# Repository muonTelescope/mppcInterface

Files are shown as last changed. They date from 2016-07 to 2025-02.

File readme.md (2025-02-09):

[headerIMG]

# MPPC Interface
Measuring and logging photon level light sources is a large part of high energy physics instrumentaiton. This board was created to power and collect data from eight MPPC (Multi Pixel photon counters) or SiPM (Silicon Photomultiplers). Provide coincidence logic and log the data out to a Raspberry Pi.

[img]

This is the main conntroller board of the muon telescope project. This board aimts to replace the current tools used

This is the technical manual for anyone wanting to modify, hack, remix, or program their own SiPM readout. The manual goes into fine detail about construction, assembly, and firmware which should encompass all basic knowledge.

## TOC

## Design
THe design was based off a combiniation of topologies from [sPhenix] design, our previous hardware iterations, and new needs in this version. The MPPCs need a very stable high voltage bias voltage that can be controled over this range in sub-milivolt steps. 

[topologyDiagarm]

This is done thoug hthe top high voltage being controalbe in 1V steps and is common across all eight chanels and a eight channel bottom DAC that provides a controlable virtual ground seperately for each channel.

The anode signal is then sent though a high amplification instrumentation amplifier and then sent to the FPGA's schmitt inputs. The conicidence logic is then done in the FPGA and its outputs are mapped to interupt vectors on the host machine.

### Components
Component selection was built off previous verisons, and the specific use case  of driving [Hamamtsu]'s MPPCs. The major ICs and other unique componets will be descibed below.

#### High Voltage Boost
*Maxim Semiconducr's* [MAX1932] has proven itself with proper layout in pervious interations of the design to provide a stable, controlable, low ripple high voltage for avalanche photodidoes. 

THe chip interanlly has a boost controller, current sensing for a current limit, and a 8b DAC that can be tied in to set the voltage over SPI.

#### Bottom DAC
The other half of the bias voltage is handled by the *Texas Instument* [DAC60508] 8 channel 12b (with a direct drop in replace for up to 16b) digital to analog converter. The linear regulation inside provides a stable output, and using the internal `2.5 V` precsion refrence LSB steps of `0.6 mV` are achived. THe output is highly linear and monotonic. 

The power consuption is also low at `0.6mA/ch` for future power constrained applicaitons.

### Schematic
### Layout
### Mechanics

## Firmware
### High Voltage
### Bottom DAC
### FPGA burning
### Compiling
### Flashing

## Gateware
### Pin connections
### Logic
### Compiling
### Flashing

## Setup
Download and flash a copy of the [Raspberry Pi OS](https://www.raspberrypi.com/software/) using either `dd` or the *Raspberry Pi imager* software.

### Raspberry Pi imager
Select the Raspberry Pi OS Lite and in advanced configuration menu (CTRL+SHIFT+X) enable ssh and add the WiFi credentials if the device will be connected over wireless network.

This video also shows using the software to flash a SD card [How to use Raspberry Pi Imager](https://www.youtube.com/watch?v=ntaXWS8Lk34)

### Advanced install with `dd`
Be very careful using `dd` to copy the image to the SD card. `dd` is a direct bit copy from the imput file to the output file and will indescriminately write over any drives without any checks or protection.

```bash
df -h
sudo umount sdx
sudo dd bs=4M if=<imgPath.img> of=/dev/sdx
```

Enable ssh by creating a blank `ssh` file in the root directory called *boot*.
```bash
cd boot
touch ssh
```

To setup connectingto WiFi on boot, a `/boot/wpa_supplicant.conf` file is created that is automatically copied over to `/etc/wpa_supplicant/wpa_supplicant.conf` on the next boot. 

```bash
nano /boot/wpa_supplicant.conf
```

And add in the relevant configuration.

```
ctrl_interface=DIR=/var/run/wpa_supplicant GROUP=netdev
country=<Insert 2 letter ISO 3166-1 country code here>
update_config=1

network={
 ssid="<Name of your wireless LAN>"
 psk="<Password for your wireless LAN>"
}
```

Insert the SD card into the Raspberry Pi, connect the ethernet cable (if connecting over wired network), and power (unless connecting though POE) and connect to the device using ssh.

You can figure out the IP address in several ways on linux you can use `nmap` or `arp` to search for the Raspberry Pi foundation's OUID (`DC:A6:32` for Raspberry Pi 4, `B8:27:EB` otherwise) on your local subnet. 

```bash
nmap -sP 192.168.1.0/24 | awk '/^Nmap/{ip=$NF}/B8:27:EB/{print ip}'
```

```bash
arp -na | grep -i b8:27:eb
```

For Windows
```cmd
arp -a | findstr b8-27-eb
```

It is also possible to ping a new install with the default hostname if DNS or the bonjour service has the device in its tables.

```bash
ping raspi
```

### Bootstrap
The setup script in the root directory can be run to set up a Raspberry pi from scratch. 

Connect to the raspberry pi using the IP adress found.
```bash
ssh pi@192.168.1.*
sudo apt install -y git
```

```bash
git clone https://github.com/muonTelescope/mppcInterface.git
cd mppcInterface
```

The root directory includes a setup script that updates the operationg system, sets up accounts, installs the toolchain, and enables all required modules. On cloning th repository on the Raspberry Pi, this file shoud be made executable and run.

```bash
chmod +x setup.sh
sudo ./setup.sh
```

expand filwsystem, not needed as pi does it on boot now.

Working buildsystem for gateware
```
Yosys 0.9+3981 (git sha1 7d2097b0, clang 7.0.1-8+rpi3+deb10u2 -fPIC -Os)
arachne-pnr 0.1+328+0 (git sha1 c40fb22, g++ 8.3.0-6+rpi1 -O2)

```

By default the spidev driver on raspberry pi has a maximum transfer size of 4096 bytes.
That might cause problems with this software so to change the default buffersize add spidev.bufsiz=65536 to /boot/cmdline.txt and reboot.
Where 65536 is the maximum size you want to allow.

get mac adress to set hostname
```bash
cat /sys/class/net/eth0/address | cut -d: -f4- | sed 's/://g' | tr [:lower:] [:upper:]
```

channelSelect.sh
```bash
#!/bin/bash

dtparam spi=off

gpio mode 6  out  # CS_DAC
gpio mode 23 out  # CS_MAX1932
gpio mode 5  out  # CS_FPGA

gpio write 6  1
gpio write 23 1
gpio write 5  1

sleep 2

gpio mode 12 out # MOSI
gpio mode 13 out # MISO
gpio mode 14 out # SCK

gpio write 12 $1
gpio write 13 $2
gpio write 14 $3

sleep 2
#rmmod spi_bcm2835
#modprobe spi_bcm2835

dtparam spi=on
```

softwareSerial read python
```python
import sys
import time
import difflib
import pigpio
import datetime
import binascii

RX=17

try:
        pi = pigpio.pi()
        pi.set_mode(RX, pigpio.INPUT)
        pi.bb_serial_read_open(RX, 115200, 8)

        print "DATA - SOFTWARE SERIAL:"
        while 1:
                (count, data) = pi.bb_serial_read(RX)
                if count:
			print str(datetime.datetime.now()) + " " +  str(binascii.hexlify(data))
                time.sleep(0.5)

except Exception as e:
	print(e)
        pi.bb_serial_read_close(RX)
        pi.stop()
```

A controller board for 

This is a continuation of a long process, over five years at this point. It is also part of a much broader set of tools and parts that make up the Muon Telesecope.

## Design

## Hardware
There are three main sections to the hardware. High voltage generation and control, Analog front end, and digital logic conatined in the FPGA.

### Bias Voltage
The MPPCs requre a bias of around 80V (varies greatly by model) with very low ripple and high precision. The gain of the sensors varies with respect to the voltage put across them and even a deviation of 10mV has a significat impact on the gain. The gain is also a function of ambient temperature and the bias needs to be controlabe to within a mV to adjust the gain as temperature changes.

[Gain vs Bias]
[Gain Vs temp chart]

The bias voltage is set though a top high voltage rail and a bottom DAC. This approach allows for a very high precision on the bottom dac along with the range on the top HV. With a 16b DAC, steps of under 100uV are possible, whcih is below the accuracy of most of the rest of the supply

For example to set the voltage to 78.434 the top rail is set to its minimal on voltage to ensure there is never a risk of a forward bias (although with the HV off the output is at 4.5V, the input voltage save the shotky didode drop so the risk is only there if the dac is ser to near its max voltage which may still be below the conduction voltage of the MPPC), then the bottom rail can be set to 1.566V, followed by the HV rail being set to 80V providing a voltage diffreential of 78.434 across the sensor.

#### HV Rail
The top high voltage rail is created using Maxim's [MAX1932] APD bias boost converter. This IC provides a low ripple 5V input to 55V to 110V output (design configurable to 20V-100V) with 8b digital control over SPI and built in current limiting set at 2.5mA.

Using a high amount of filtering on the inputs and outpurs, large bulk capacitors, a tight layout, EMC shields, and sectioned off ground and power planes, the output ripple as well as emitted noise is reduced significantly. The output ripple is well below 1mV.

The voltage range, and step size is dictated with setting R2, R3, and R4. The minimum and maximum voltage set using the equations for on page 7 of the datasheet, and there are 8 bits (256) intermediate values that are possible. The high switching portion was designed with general SMPS design requirements (short high current loops, separated ground planes, EMI shielding) providing a low ripple output (<5mVpp ripple) and no significant back EMF.

The Setting resistors are 0.01% and the chip provides a 0.5% accuracy which needs to be calibrated. The calibration and certification procedure is provided in another section of documention.

[Table of set R values and the range they create]
[Fucntion of byte to voltage with perfect resistors]

#### Bottom DAC

The "Bottom DAC" is the term used to describe the arrangement where the voltage supply at the anode of a reverse biased SiPM is used to "subtract" from the top bias voltage. It is implemented with a eight channel 16b [DAC80508] by Texas Instruments. This provides independent control with a 5V range for each of the eight chanels. 

### Analog Front End
The analog front end amplifier is also highly specilized. The design condierations to be considered are considerable and require specilized parts [MPPC AFE talk]. In the end the selection is a very high bandwidth low noise instrumentation amplifier with a 400x gain. The [OPA846] has a high slew rate of 625V/us and a gain bandwith product of 1.75Ghz providing a adequate bandwith of ~4.3Mhz with our gain. 

[Outfput waveform]

This provides waveforms from over xx photons to reach the 1.4V lower schmitt threadhold of the digital logic 3.3V/2-100mV. 

[Photn and gain calculation]
x photons needed * 40% efficency * 	1.7E6 * 1.602E-19C / nS?	

The aplifier's input in coupled with a DC blocking capacitor and routed very tightly on a single layer to reduce noise and emissions that will easily be amplified with such a high gain. The gain of 400x is acivhed with a 20k and 50R positive feedback in a non-inverting configuration. The output is AC coupled to make sure the output has minimal capacitive loading especially since we are only looking for a hihg speed signal output.

[Routing of AFE]

#### Digital Logic
The digital logic is done with a FPGA and can be reconfigured though gateware based on the detector configuration. The eight channels are connected to the GPIO and the schmitt inputs act as discriminators. The rest of the lines are run to three LEDs that can be used for indication and to the GPIO of the Raspberry Pi.

#### Power supply
The general supply rails are provide dby the host Raspberry pi connector. The entire board uses about 1W across all the modules. The 5V supply, after some back EMF filtering is provided to the HV supply as well as the AFE power module. The 3.3V is used on the FPGA and the signaling Power supply of the DAC.

Very stable +-5V rails are required for the analog front end to have have the low noise it needs. The Analog \pm 5V is seperated to its own power planes and is hevily filtered and decoupled ensuring very little noise that would show amplifed on the output. This supply is generated thougha commerical module which is rated at a low ripple and switching frequency.

A 1.2V linear regulator provides the core voltage to the FPGA.

#### Mounting
The hat is attached to the raspberry pi with four 2.6mm mounting holes form M2.5 screwas nad standoffs. A M2.5x11 standoff provides mounting and clearence. The size of the module is showin in the drawing below, it is the same sizing as a raspberry pi zero.

## Firmware
This repository contains firmware in the form of C++ libraries that can be linked into your own code as well as a basic data logging application that sets up everything and logs the counts to a file. 

#### High Voltage
The SPI bus is connected directly to the MAX1932. Chip select is active low and data is sent MSB (most significant bit first). Sending bytes to it sets the voltage. Setting them to 0x00 turns off the DC-DC converter portion. As values increase to 0xFF (256), the output voltage falls linearly.

```Arduino
//Example Arduino code that loops through all voltages.
//SCLK --> Pin 13 for Uno or Duemilanove
//DIN ---> Pin 11 for Uno or Duemilanove

#include <SPI.h>
#define CS 2 //Any pin

void setup(){
	Serial.begin(9600);
	pinMode(CS, OUTPUT);
	digitalWrite(CS, HIGH);
	SPI.begin();
	SPI.setBitOrder(MSBFIRST);
}

void loop(){
	for(int i = 0 ; i < 256 ; i++){
		digitalWrite(CS, LOW);
		SPI.transfer(i);
		digitalWrite(CS, HIGH);
		Serial.println(i);
	}
}
```

---
In the config file the voltage is set for 25*. 

#### DAC

## Gateware

#### Flashing

##### Clearing
##### Burning
##### File format

##### Compilation
###### Yosys
###### AracnePNR

## Absolute Maximum ratings
## Gaurenteed Ratings
## Manufacturing
### BOM
### PCB Assembly
The board has three fiducials and 1.152mm tooling holes for automated assembly.
### Artwork
### Labeling
## Safety
## Certifications
## Licence
## Attributions

- HV Calibration procedure and certification.

Glossary
MPPC Multi pixel photon counter, Hamamtsu Photonics's 
SiPM
DAC
Bias

# Old Version of docs

A single assembled board breaks out singals and provides all the interfaces that 4 [MPPC Sesnor](https://github.com/Sawaiz/mppcSensor) boards need. The power to each module is supplied via the [MPPC high voltage](https://github.com/Sawaiz/mppcHighVoltage) modules
attached board. It is able to be run independently for testing and debugging, or on a backplane with many others for more channels.

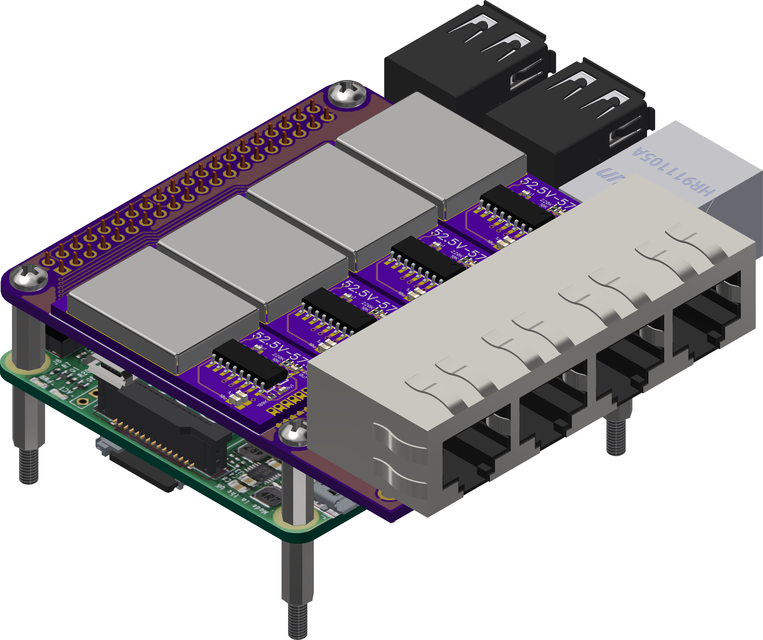
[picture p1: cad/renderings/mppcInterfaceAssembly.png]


## Expansion Format

### SPI
The SPI exapansion format is designed to be infinetly expandable up to the signal propgation length and capactive loading. 

The Design of the SPI system is chained shift registers. The shift registers 

SPI EEPROM lies on each expansion board and has the code needed to interface with it (this sounds beautiful, really).
The EEPROM contains the device enumeration and drivers for all the 8 slots on its adress.
Master downloads drivers 

### I2C

## Hardware
The board attaches directly to a Raspberry Pi using the centered GPIO headers. The Raspberry Pi is mounted to the board via four standoffs. It is a stand alone board requiring no backplane. This board can be mounted via the M5 screw holes around the edge.

### Power
Power is supplied through two pins on the edge connector, or via the micro USB port on board. There is a 600mA buck regulator that provides power when the USB port is used. The board should be powered by 3.3V and a negative power supply module with convert it to -3.3V for the biasing for the op-amps.

### High Voltage
High voltage is supplied through a daughter board. Each channel has a independent voltage source that can be temperature modulated and monitored via the on board ADC. for more information about the modules, read [here](https://github.com/Sawaiz/mppcHighVoltage).

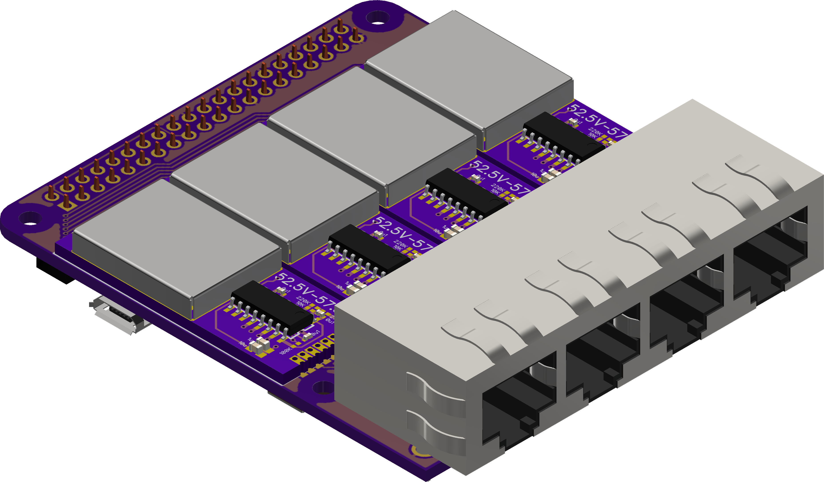
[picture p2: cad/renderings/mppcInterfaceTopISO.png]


### Microcontroller
The side of the board has a Arduino compatible ([ATmega328](http://www.atmel.com/images/Atmel-8271-8-bit-AVR-Microcontroller-ATmega48A-48PA-88A-88PA-168A-168PA-328-328P_datasheet_Complete.pdf)) microcontroller, along with a USB part, USB to UART converter and other supporting circuitry. The button is connected to the reset pin. The programing port on board is a Tag-Connect 6 pin, and is only used for programing the Arduino bootloader.

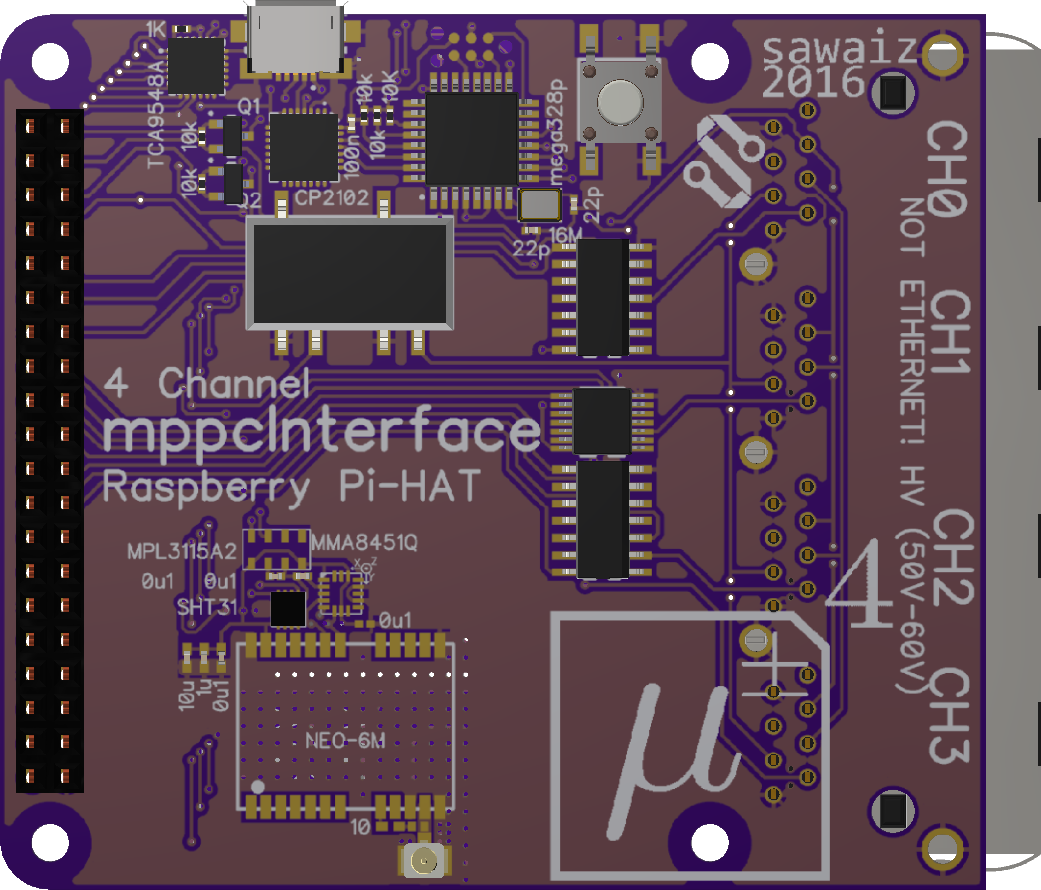
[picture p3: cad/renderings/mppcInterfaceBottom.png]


### I2C Switch
As all the ADC modules on the daughter boards have the same address, a 8 channel I2C switch ([TCA9548A](http://www.ti.com/lit/ds/symlink/tca9548a.pdf)) is used to communicate to them independently. The pins attached to it are referenced as master, as the microcontroller is acting as the master controlling it.

## BOM
The bill of materials is availible in [bom.csv](bom.csv) and is copied into a table below.

| Ref Des                                                                                          | Qty | Manufacturer          | MPN                 | Description                      |
| ------------------------------------------------------------------------------------------------ | ---:| --------------------- | ------------------- | -------------------------------- |
| C1                                                                                               | 1   | Wuerth Elektronik     | 885012105011        | CAP CER 0.22UF 10V X5R 0402      |
| C2                                                                                               | 1   | Wuerth Elektronik     | 885012208116        | CAP CER 0.047UF 100V X7R 1206    |
| C3 C5 C7 C9 C11 C13 C15 C17                                                                      | 8   | Wuerth Elektronik     | 885012205016        | CAP CER 0.047UF 10V X7R 0402     |
| C19                                                                                              | 1   | Samsung               | CL21B105KOFNNNG     | CAP CER 1UF 16V X7R 0805         |
| C20                                                                                              | 1   | Samsung               | CL31B105KCHNNNE     | CAP CER 1UF 100V X7R 1206        |
| C21                                                                                              | 1   | AVX                   | 22201C106MAT2A      | CAP CER 10UF 100V X7R 2220       |
| C22 C24                                                                                          | 2   | Murata                | GRM155C80J106ME11D  | CAP CER 10UF 6.3V X6S 0402       |
| C29 C28 C34 C33 C39 C38 C44 C43 C49 C48 C54 C53 C59 C58 C64 C63                                  | 16  | Wuerth Elektronik     | 885012105016        | CAP CER 0.1UF 16V X5R 0402       |
| C23 C32 C31 C27 C26 C37 C41 C42 C36 C4 C25 C6 C30 C8 C35 C10 C40 C12 C45 C14 C50 C16 C55 C18 C60 | 25  | Samsung               | CL05A105MP5NNNC     | CAP CER 1UF 10V X5R 0402         |
| C65                                                                                              | 1   | TDK                   | C1005X5R1A335M050BC | CAP CER 3.3UF 10V X5R 0402       |
| R1                                                                                               | 1   | Stackpole Electronics | RMCF0402FT1M13      | RES 1.13M OHM 1% 1/16W 0402      |
| R2                                                                                               | 1   | Stackpole Electronics | RMCF0402JT20R0      | RES 20 OHM 5% 1/16W 0402         |
| R3                                                                                               | 1   | Yageo                 | RT0402BRD072K49L    | RES SMD 2.49KOHM 0.1% 1/16W 0402 |
| R4                                                                                               | 1   | Yageo                 | RC0402FR-07806RL    | RES SMD 806 OHM 1% 1/16W 0402    |
| R5                                                                                               | 1   | Yageo                 | RT0402BRD07100KL    | RES SMD 100K OHM 0.1% 1/16W 0402 |
| R6                                                                                               | 1   | TE Connectivity       | CPF0402B23R7E1      | RES SMD 23.7 OHM 0.1% 1/16W 0402 |
| R7 R12 R17 R22 R27 R32 R37 R42                                                                   | 8   | Yageo                 | RT0402DRE071KL      | RES SMD 1K OHM 0.5% 1/16W 0402   |
| R8 R9 R13 R14 R18 R19 R23 R24 R28 R29 R33 R34 R38 R39 R43 R44                                    | 16  | Panasonic             | ERJ-2RKD49R9X       | RES SMD 49.9 OHM 0.5% 1/16W 0402 |
| R10 R15 R20 R25 R30 R35 R40 R45                                                                  | 8   | Stackpole Electronics | RNCF0402DTE20K0     | RES 20K OHM 0.5% 1/16W 0402      |
| R11                                                                                              | 1   | Stackpole Electronics | RMCF0402FT499K      | RES 499K OHM 1% 1/16W 0402       |
| D2                                                                                               | 1   | ON Semiconductor      | FDLL4148            | DIODE GEN PURP 100V 200MA LL34   |
| J1 J2 J3 J4 J5 J6 J7 J8                                                                          | 8   | Hirose                | U.FL-R-SMT-1(40)    | CONN U.FL RCPT STR 50 OHM SMD    |
| J9                                                                                               | 1   | Sullins               | SFH11-PBPC-D20-ST-BK| CONN HDR 40POS 0.1 GOLD PCB      |
| J10                                                                                              | 1   | FCI                   | 54601-906WPLF       | CONN MOD JACK 6P6C R/A UNSHLD    |
| J11                                                                                              | 1   | Harwin                | M20-8760542         | CONN HEADER SMD 10POS 2.54MM     |
| J12                                                                                              | 1   | FCI                   | 54602-908LF         | CONN MOD JACK 8P8C R/A UNSHLD    |
| L1                                                                                               | 1   | Bourns                | SRN4018-151M        | FIXED IND 150UH 320MA 2.4 OHM    |
| L2                                                                                               | 1   | Taiyo Yuden           | CBC3225T102KR       | FIXED IND 1MH 100MA 13 OHM SMD   |
| Q1                                                                                               | 1   | ON Semiconductor      | BSS123L             | MOSFET N-CH 100V 0.17A SOT-23    |
| U1                                                                                               | 1   | Texas Instruments     | DAC60508ZRTER       | IC DAC 12BIT V-OUT 16WQFN        |
| U2                                                                                               | 1   | Microchip             | MIC5504-1.2YM5-TR   | IC REG LINEAR 1.2V 300MA SOT23-5 |
| U3                                                                                               | 1   | Texas Instruments     | LM27761DSGR         | IC REG CHARGE PUMP ADJ 8WSON     |
| U4                                                                                               | 1   | Nexperia              | 74HC595PW-112       | IC 8BIT SHIFT REGISTER 16TSSOP   |
| U5                                                                                               | 1   | Maxim Integrated      | MAX1932ETC+T        | IC REG CTRLR FBR OPT 1OUT 12TQFN |
| U6 U7 U8 U9 U10 U11 U12 U13                                                                      | 8   | Texas Instruments     | OPA846IDBVT         | IC OPAMP VFB 1 CIRCUIT SOT23-5   |
| U14                                                                                              | 1   | Lattice Semiconductor | ICE40LP384-SG32     | IC FPGA 21 I/O 32QFN             |

Aslo availible though [octopart](https://octopart.com/bom-tool/T0iNvVYe) 

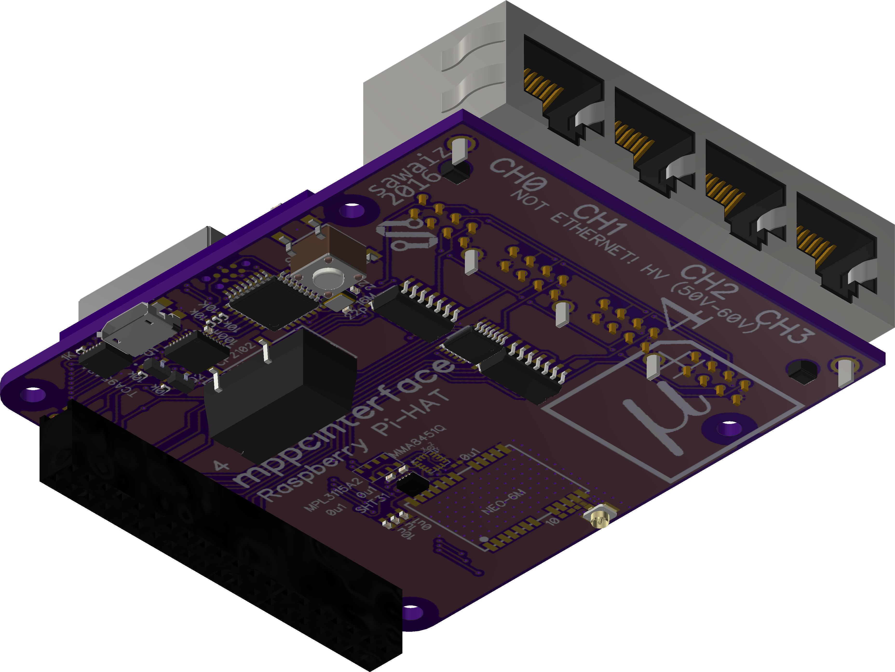
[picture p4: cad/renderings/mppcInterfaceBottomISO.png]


## Software
The device acts as both a master and slave device. It takes instructions from an external I2C bus, and executes them on the AVR microcontroller to set voltages, provide telemetry, and preform closed loop control.

### AVR
The microcontroller on board takes commands sent to the whole module, and forwards them to each daughterboard. It primary control loop involves reading the temperature, finding the associated required bias voltage based on the temperature and setting the voltage on the high voltage supply, then checking if the output voltage is within specification of the required output, and fixing it if not. This loops for all eight channels. Otherwise there is an instruction queue of commands that come into the module.

### Module
The master can communicate to up to 128 slave devices the address is set within software. The master can request the temperature, or current voltage of any of the eight channels on board, select between different voltage to temperature curves, and set the bias voltage, or pulse the LED on the modules.

[mppcInterfaceAssembly]:  cad/renderings/mppcInterfaceAssembly.png  "View of Back of Board"
[mppcInterfaceTopISO]:    cad/renderings/mppcInterfaceTopISO.png    "Direct front view"
[mppcInterfaceBottomISO]: cad/renderings/mppcInterfaceBottomISO.png "Board rendering with EMI shield"
[mppcInterfaceBottom]:    cad/renderings/mppcInterfaceBottom.png    "Board rendering with EMI shield"

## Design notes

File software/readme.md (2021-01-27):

Install nginx
Run webserver with static site for diognostics and settings
Split up files into 1 day increments

Static files with a rest API
    Express
    Top Voltage
    Bottom DAC
    Configuration file selection
    ip adress
    battery percentage
    uptime
    gps
    hostname
    shutdown
mantain local arrays of data
new local log file for each day as backup

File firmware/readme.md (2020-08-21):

## 1 day test 8/18
0x98, 78.56V - Test voltage 
CH0 - 
CH1 - 

## Multi day test 8/19
0x92, 79.775V
CH0 - 0x7880
CH1 - 0x8000

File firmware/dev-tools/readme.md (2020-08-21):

# Development Tools
Development and testing tools run from command line and interact directly with the hardware. The tools provide everything that one can do from the web interface.

## Structure
The code is copied and trimmed down from what is used on the website backend, and is written in javascript. There are bash files that call the functions through nodejs and they make sure it is run with proper permissions and enough arguments.

## Installation
Install the required packages with 
```bash
npm install
```
As these integrate with hardware on a raspberry pi, you will need to build/compile them on the Broadcom chip itself. After the install, you should have a "node_modules" folder in the root project directory.

## Run
Each module is different and requires its own function call. All need to be run as root as hardware GPIO access is privileged

### Current Status
Prints out all the voltages, temperatures, and targets of all eights channels on slave address of 0x08
```bash
sudo ./voltageDump.sh
```
Response is a markdown compatible table
```md
|Board   0x08|  Channel 0 |  Channel 1 |  Channel 2 |  Channel 3 |  Channel 4 |  Channel 5 |  Channel 6 |  Channel 7 |
|------------|------------|------------|------------|------------|------------|------------|------------|------------|
|Target   (V)|   0.000000 |  55.110000 |  55.120000 |  55.170000 |   0.000000 |   0.000000 |   2.887680 |   0.000000 |
|Voltage  (V)|   4.484427 |  55.589808 |  55.323148 |  55.523284 |   0.000000 |   0.000000 |   0.000000 |   0.000000 |
|Temp     (C)|  11.174347 |  16.505951 |  21.479584 |  18.281768 |   0.000000 |   0.000000 |   0.000000 |   0.000000 |

```
The current voltage may not match the target. The firmware on each board should be temperature compensating the bias voltage depending on temperature. The target refers to the voltage at 25C.

### Sensor Temp
Given the channel on a board connected with the slave address of 0x08, it prints out the temperature in degrees Celsius.
```bash
sudo ./getTemp.sh <channel>
```
For example, to read the temperature from the sensor connected to the third port (channel 2, they index from 0).
```bash
sudo ./getTemp.sh 2
```
And the response is just
```bash
21.44754
```

### Current Voltage
Given the channel on a board connected with the slave address of 0x08, it prints out the voltage output from the power supply.
```bash
sudo ./getVoltage.sh <channel>
```
For example, to read the voltage from the sensor connected to the third port (channel 2, they index from 0).
```bash
sudo ./getVoltage.sh 2
```
And the response is just
```bash
55.322936
```

### Read Target Voltage
Given the channel on a board connected with the slave address of 0x08, it prints out the target voltage at 25C.
```bash
sudo ./getTarget.sh <channel>
```
For example, to read the target for the third port (channel 2, they index from 0).
```bash
sudo ./getTarget.sh 2
```
And the response is just
```bash
55.12
```

### Set Target Voltage
Given the channel on a board connected with the slave address of 0x08, it sets the target voltage at 25C.
```bash
sudo ./setTarget.sh <channel>
```
For example, to set the target for the third port (channel 2, they index from 0) to 55.12V.
```bash
sudo ./setTarget.sh 2 55.12
```
There is no response. Reading the target voltage can be used to confirm that the target was changed.

### GPS
If a GPS module is populated, running
```bash
./gpsData.sh
```
Will return
```javascript
{ time: 2016-11-14T07:20:12.000Z,
  latitude: 33.7535,
  longitude: -84.38733333333333,
  altitude: 322.9,
  speedKph: 0.424,
  trueCourse: 'N/A',
  PDOP: 12.12,
  HDOP: 4.79,
  VDOP: 11.13,
  vaild: true }
```
### SHT3X
SHT3X is a temperature and humidity module.
```bash
sudo ./sht3x.sh
```
Returns a JSON formatted object with temperature is Celsius, Fahrenheit, and relative humidity in percent
```javascript 
{ temp: 30004,
  humdity: 18553,
  temp_F: 95.21698329137104,
  temp_C: 35.1205462729839,
  RH: 28.31006332494087 }
```

### MPL3115A2
The MPL3115A2 is a temperature and pressure sensor.
```bash
sudo ./mpl3115a2.sh
``` 
Returns a JSON formatted object containing pressure in pascals and temperature in degrees Celsius
```javascript
{ pressure_H: 94,
  pressure_C: 93,
  pressure_L: 176,
  temp_H: 36,
  temp_L: 128,
  pressure: 386523,
  pascals: 96630.75,
  temp: 584,
  temp_C: 36.5 }
```

### Log Data
The log data module takes two additional parameters. The duration between each log in milliseconds, and the directory location to write the file to.
```bash
sudo ./logdata.sh <duration (ms)> <file location>
```
As the program runs, it also prints the contents of what it writes to the logfile to STDOUT. For example, to run the script with one minute time intervals and store the logfile in a parent directory logs folder run the following.
```bash
sudo ./logData.sh 60000 ../logs/
```
Below is an example of the file `2017-04-24T21:00:07.503Z.log`
```
date,Zero and One,Zero and Two,Zero and Three,One and Two,One and Three,Two and Three,Zero,One,Two,Three,
2017-04-24T21:01:07.625Z,0,0,0,0,37,0,0,830,0,688,
2017-04-24T21:02:07.634Z,0,0,0,0,44,0,0,843,0,725,
2017-04-24T21:03:07.639Z,0,0,0,0,40,0,0,869,0,717,
2017-04-24T21:04:07.643Z,0,0,0,0,36,0,0,810,0,688,
2017-04-24T21:05:07.647Z,0,0,0,0,42,0,0,860,0,673,
2017-04-24T21:06:07.652Z,0,0,0,0,47,0,0,888,0,728,
```

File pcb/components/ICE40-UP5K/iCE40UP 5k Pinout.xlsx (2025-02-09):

# Pin Out For iCE5UP5K (iCE40 UltraPlus - 5K)
# Revision 0.4 - Remove FWG49
# Revision 1.1 - Fix RGB pins, swapped C5 & A5 pins as well as 39 & 41
# Updated Jun 19, 2017
FNC | Pin Type | BANK | Differential Pair | UWG30 | SG48
IOB_0a | PIO | 2 |  | E5 | 46
IOB_2a | DPIO | 2 | TRUE_of_IOB_3b | D5 | 47
IOB_3b_G6 | DPIO/GBIN | 2 | COMP_of_IOB_2a | F5 | 44
IOB_4a | DPIO | 2 | TRUE_of_IOB_5b | - | 48
IOB_5b | DPIO | 2 | COMP_of_IOB_4a | - | 45
IOB_6a | PIO | 2 |  | - | 2
IOB_8a | DPIO | 2 | TRUE_of_IOB_9b | - | 4
IOB_9b | DPIO | 2 | COMP_of_IOB_8a | E4 | 3
IOB_10a | DPIO | 1 | TRUE_of_IOB_11b | C3 | -
IOB_11b_G5 | DPIO/GBIN | 1 | COMP_of_IOB_10a | F4 | -
creset_b | CONFIG | 1 |  | F3 | 8
IOB_12a_G4_CDONE | CONFIG/DPIO/GBIN | 1 | TRUE_of_IOB_13b | D3 | -
CDONE | CONFIG | 1 |  | - | 7
IOB_13b | DPIO | 1 | COMP_of_IOB_12a | E3 | 6
IOB_16a | PIO | 1 |  | - | 9
IOB_18a | PIO | 1 |  | - | 10
IOB_20a | PIO | 1 |  | - | 11
IOB_22a | DPIO | 1 | TRUE_of_IOB_23b | - | 12
IOB_23b | DPIO | 1 | COMP_of_IOB_22a | - | 21
IOB_24a | DPIO | 1 | TRUE_of_IOB_25b | B1 | 13
IOB_25b_G3 | DPIO/GBIN | 1 | COMP_of_IOB_24a | F2 | 20
IOB_29b | PIO | 1 |  | - | 19
IOB_31b | PIO | 1 |  | - | 18
IOB_32a_SPI_SO | DPIO/CONFIG_SPI | 1 |  | F1 | 14
IOB_33b_SPI_SI | DPIO/CONFIG_SPI | 1 |  | E1 | 17
IOB_34a_SPI_SCK | DPIO/CONFIG_SPI | 1 |  | D1 | 15
IOB_35b_SPI_SS | DPIO/CONFIG_SPI | 1 |  | C1 | 16
VCCPLL | VCCPLL |  |  | B2 | 29
IOT_36b | DPIO/I3C | 0 | COMP_of_IOT_37a | A1 | 25
IOT_37a | DPIO/I3C | 0 | TRUE_of_IOT_36b | A2 | 23
IOT_38b | DPIO | 0 | COMP_of_IOT_39a | - | 27
IOT_39a | DPIO | 0 | TRUE_of_IOT_38b | - | 26
IOT_41a | PIO | 0 |  | - | 28
IOT_42b | DPIO | 0 | COMP_of_IOT_43a | - | 31
IOT_43a | DPIO | 0 | TRUE_of_IOT_42b | - | 32
IOT_44b | DPIO | 0 | COMP_of_IOT_45a | - | 34
IOT_45a_G1 | DPIO/GBIN | 0 | TRUE_of_IOT_44b | - | 37
IOT_46b_G0 | DPIO/GBIN | 0 |  | B3 | 35
IOT_47a | PIO | 0 |  | A4 | -
IOT_48b | DPIO | 0 | COMP_of_IOT_49a | - | 36
IOT_49a | DPIO | 0 | TRUE_of_IOT_48b | - | 43
IOT_50b | DPIO | 0 | COMP_of_IOT_51a | - | 38
IOT_51a | DPIO | 0 | TRUE_of_IOT_50b | - | 42
RGB2 | LED | 0 |  | C5 | 41
RGB1 | LED | 0 |  | B5 | 40
RGB0 | LED | 0 |  | A5 | 39
GND | GND | GND |  | B4 | Paddle
GND | GND | GND |  | E2 | Paddle
GND | GND | GND |  | - | Paddle
VCC | VCC | VCC |  | C2 | 5
VCC | VCC | VCC |  | - | 30
VCCIO_0 | VCCIO | 0 |  | A3 | 33
SPI_Vccio1 | VCCIO | 1 |  | D2 | 22
VCCIO_2 | VCCIO | 2 |  | C4 | 1
VPP_2V5 | VPP | VPP |  | D4 | 24
*SG48 GND is connected to package paddle

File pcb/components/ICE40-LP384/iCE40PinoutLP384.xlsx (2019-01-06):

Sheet: Pinout
iCE40 Pinout LP384
Ball Function | Pin Type | Bank | (SG32) 32-Pin QFN Ball Number | (CM36) 36-Ball ucBGA Ball Number | (CM49) 49-Ball ucBGA Ball Number
IOL_1A | DPIO | 3 | - | - | -
IOL_1B | DPIO | 3 | - | - | -
IOL_2A | DPIO | 3 | 2 | B1 | A1
IOL_2B | DPIO | 3 | 1 | A1 | B1
IOL_3A | DPIO | 3 | - | - | C2
IOL_3B | DPIO | 3 | - | - | B2
IOL_4A | DPIO | 3 | 5 | C2 | C1
IOL_4B_GBIN7 | GBIN | 3 | 6 | C1 | D2
IOL_5A_GBIN6 | GBIN | 3 | 8 | D1 | E2
IOL_5B | DPIO | 3 | 7 | E1 | D1
IOL_6A | DPIO | 3 | - | - | -
IOL_6B | DPIO | 3 | - | - | -
IOL_7A | DPIO | 3 | - | - | F1
IOL_7B | DPIO | 3 | - | - | D3
IOL_8A | DPIO | 3 | - | - | G1
IOL_8B | DPIO | 3 | - | - | F2
IOB_16 | PIO | 2 | - | - | -
IOB_17 | PIO | 2 | - | - | -
IOB_18 | PIO | 2 | - | - | -
IOB_19 | PIO | 2 | - | - | -
IOB_20 | PIO | 2 | - | F2 | G3
IOB_21_GBIN5 | GBIN | 2 | - | E2 | F3
IOB_22_GBIN4_CBSEL0 | GBIN | 2 | - | E3 | F4
IOB_23_CBSEL1 | PIO | 2 | - | F3 | G4
CDONE | CONFIG | 2 | 11 | C4 | D5
CRESET_B | CONFIG | 2 | 10 | F4 | G5
IOB_24_SDO | SPI | SPI | 12 | E4 | F5
IOB_25_SDI | SPI | SPI | 13 | F5 | G6
IOB_26_SCK | SPI | SPI | 15 | E5 | F6
IOB_27_SS | SPI | SPI | 14 | D5 | E6
VCC_SPI | SPI | SPI | 16 | F6 | G7
IOR_28 | PIO | 1 | - | - | -
IOR_29 | PIO | 1 | - | - | -
IOR_30 | PIO | 1 | - | - | -
IOR_31 | PIO | 1 | - | - | -
IOR_33 | PIO | 1 | - | E6 | F7
IOR_34 | PIO | 1 | 18 | D6 | E7
IOR_35_GBIN3 | GBIN | 1 | 19 | C5 | D6
IOR_36_GBIN2 | GBIN | 1 | 20 | B4 | D7
IOR_37 | PIO | 1 | - | B5 | C6
IOR_38 | PIO | 1 | 22 | B6 | C7
IOR_39 | PIO | 1 | 23 | C6 | C5
IOR_40 | PIO | 1 | - | - | -
IOR_41 | PIO | 1 | - | - | -
IOR_42 | PIO | 1 | - | - | -
IOR_43 | PIO | 1 | - | - | -
VPP_2V5 | VPP | VPP | 24 | A6 | B7
VPP_FAST | VPP | VPP | - | - | -
IOT_44 | PIO | 0 | - | - | A7
IOT_45 | PIO | 0 | 26 | - | A6
IOT_46 | PIO | 0 | - | - | D4
IOT_47 | PIO | 0 | 27 | - | A5
IOT_48 | PIO | 0 | - | - | A4
IOT_49_GBIN0 | GBIN | 0 | 29 | B3 | B4
IOT_50_GBIN1 | GBIN | 0 | 30 | A3 | C4
IOT_51 | PIO | 0 | - | - | A3
IOT_52 | PIO | 0 | 32 | A2 | A2
IOT_53 | PIO | 0 | 31 | C3 | B3
IOT_54 | PIO | 0 | - | - | -
IOT_55 | PIO | 0 | - | - | -
GND | GND | GND | 3 | D2 | E3
GND | GND | GND | 21 | D3 | E4
GND | GND | GND | - | D4 | E5
GND | GND | GND | - | - | -
VCC | VCC | VCC | 25 | B2 | C3
VCC | VCC | VCC | - | - | E1
VCC | VCC | VCC | - | - | -
VCCIO_0 | VCCIO | VCCIO | 28 | A4 | B5
VCCIO_1 | VCCIO | VCCIO | 17 | A5 | B6
VCCIO_2 | VCCIO | VCCIO | 9 | - | -
VCCIO_3 | VCCIO | VCCIO | 4 | - | -
VCCIO_2_3 | VCCIO | VCCIO | - | F1 | G2
NC | NC | NC | - | - | -
NC | NC | NC | - | - | -
NC | NC | NC | - | - | -
NC | NC | NC | - | - | -
NC | NC | NC | - | - | -
NC | NC | NC | - | - | -
NC | NC | NC | - | - | -
NC | NC | NC | - | - | -
NC | NC | NC | - | - | -
NC | NC | NC | - | - | -

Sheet: Revision History
Version | Date | Description
1.1 | 2013-06-27 | Removal of CM81 package. Included package ordering code.
1.0 | 2013-03-13 | Initial Release

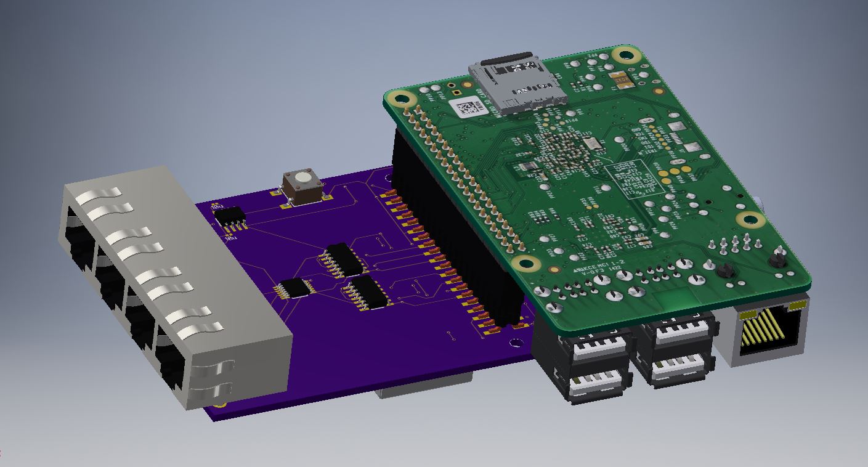
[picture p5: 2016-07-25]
cad/renderings/mppcInterfaceIso.jpg

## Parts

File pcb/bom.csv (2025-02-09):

Designator | Type | Package | Quantity | Description | MPN | LCSC | Vendor | Notes
C1 C3 C5 C9 C25 C28 C33 C30 C38 C35 C43 C40 C48 C45 C50 C53 C55 C58 C60 C63 C66 C67 | SMD | C-0402 | 22 | CAP: 0402 0u1 16V MLCC | CL05B104KO5NNNC | C1525 | Open
C11 | SMD | C-0805 | 1 | CAP: 0805 47n 100V MLCC | CL21B473KCFNNNE | C376987 | Open
C12 | SMD | C-1206 | 1 | CAP: 1206 1u 100V MLCC | CL31B105KCHNNNE | C13832 | Open
C13 | SMD | C-2220 | 1 | CAP: 2220 10u 100V MLCC | FS55X106K101EGG | C2843466 | Open
C14 C18 C17 | SMD | C-0805 | 3 | CAP: 0805 4u7 25V MLCC | CL21A475KAQNNNE | C1779 | Open
C2 C4 C6 C7 C10 C15 C16 C19 C20 C24 C26 C8 C29 C31 C34 C36 C39 C41 C44 C46 C49 C51 C54 C56 C59 C61 | SMD | C-0402 | 26 | CAP: 0402 1u 16V MLCC | CL05A105KP5NNNC | C52923 | Open
C21 | SMD | C-0402 | 1 | CAP: 0402 0u22 16V MLCC | 8.85012E+11 | C16772 | Open
C23 | SMD | C-0805 | 1 | CAP: 0805 0u1 16V MLCC | CL21B104KACNNNC | C49678 | Open
C27 C32 C37 C42 C47 C52 C57 C62 | SMD | C-0402 | 8 | CAP: 0402 0u1 100V MLCC | GRM155R62A104KE14D | C162179 | Open
C68 C22 C64 C65 | SMD | C-0805 | 4 | CAP: 0805 1u 16V MLCC | CL21B105KOFNNNG? | C28323 | Open
D3 D1 D2 | SMD | D-0402 | 3 | LED: 0402 RED | 150040RS73240 | C165980 | Open
D4 | SMD | SOD-80 | 1 | D: LL4148 100V Fast | LL4148-M-08 | C9808 | Open
J1 J2 J3 J4 J5 J6 J7 J8 | SMD | U.FL | 8 | CON: U.FL Coax | U.FL-R-SMT-1(40) | C88374 | Open
J9 | THT | 20x2 2.54mm | 1 | CON: 40pin Stacking | 1528-1385-ND | C3165 | Open
L1 | SMD | SRN4018 | 1 | IND: 150uH 350mA Sat | SRN4018-151M | C285835 | Bourns
L2 | SMD | L-1210 | 1 | IND: 1210 1mH | CBC3225T102KR | C114766 | Open
L3 L4 | SMD | L-0805 | 2 | IND: 0805 47u | LBR2012T470K | C14304 | Open
L7 L6 L5 | SMD | L-0805 | 3 | IND: 0805 10u | MLZ2012M100WT000 | C1046 | Open
Q1 | SMD | SOT-23-3 | 1 | Q: BSS123L | BSS123LT1G | C78755 | Open
R1 | SMD | R-0402 | 1 | RES: 0402 806R 1% | RMCF0402FT806R | C150511 | Open
R2 | SMD | R-0402 | 1 | RES: 0402 100K 0.1% | RT0402BRE07100KL | C525709 | Open
R3 | SMD | R-0402 | 1 | RES: 0402 2K49 0.1% | RMCF0402FT2K49 | N/A | Open
R4 | SMD | R-0402 | 1 | RES: 04002 20R 5% | RMCF0402JT20R0 | C25150 | Open
R5 | SMD | R-0402 | 1 | RES:0402 2K37 0.1% | RT0402BRD072K37L | N/A | Open
R6 R10 R14 R18 R22 R26 R30 R34 | SMD | R-0402 | 8 | RES: 0402 1K 5% | CRG0402J1K0 | C279987 | Open
R7 R8 R12 R11 R15 R16 R19 R20 R23 R24 R28 R27 R32 R31 R36 R35 | SMD | R-0402 | 16 | RES: 0402 49R9 0.1% | RT0402BRD0749R9L | C490832 | Open
R9 R13 R17 R21 R25 R29 R33 R37 | SMD | R-0402 | 8 | RES: 0402 20K 0.1% | RT0402BRD0720KL | C490819 | Open
SH1 | SMD | S03-30100300R | 1 | S03-30100300R | S03-30100300R | N/A | Harwin | Do not populate or purchase
U1 U2 U3 U4 U5 U6 U7 U8 | SMD | SOT-23-5 | 8 | AMP: OPA846 | OPA846IDBVR | C205997 | TI
U10 | SMD | SOT-23-5 | 1 | PWR: MIC5504-1.2YM5 | MIC5504-1.2YM5-TR | N/A | Microchip
U11 | SMD | TQFN-12 | 1 | PWR: MAX1932 | MAX1932ETC+T | N/A | Maxim
U12 | SMD | WQFN-16 | 1 | U: DAC60508ZRTE | DAC60508ZRTET | N/A | TI
U13 | THT | MEA1-D | 1 | PWR: MEA1D0505DC | MEA1D0505DC | N/A | MuRata
U9 | SMD | QFN32 | 1 | U: ICE40-LP384-SG32 | ICE40LP384-SG32 | N/A | Lattice

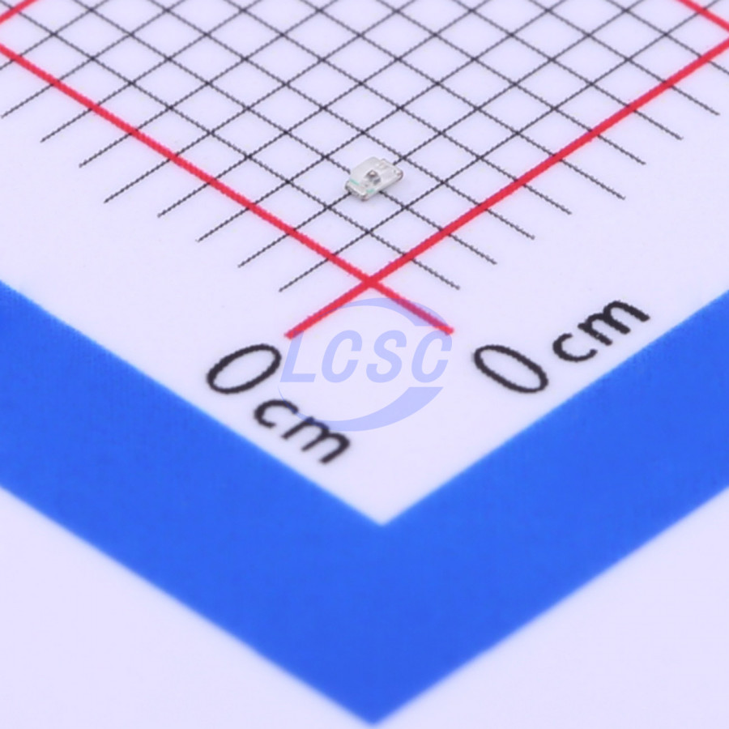
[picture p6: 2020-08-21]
pcb/components/BL-HUB37A-AV-TRB/BL-HUB37A-AV-TRB.jpg

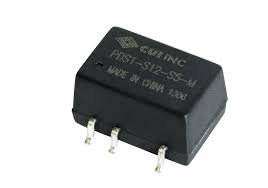
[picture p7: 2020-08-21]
pcb/components/PDS1-M/PDS1-M.jpg

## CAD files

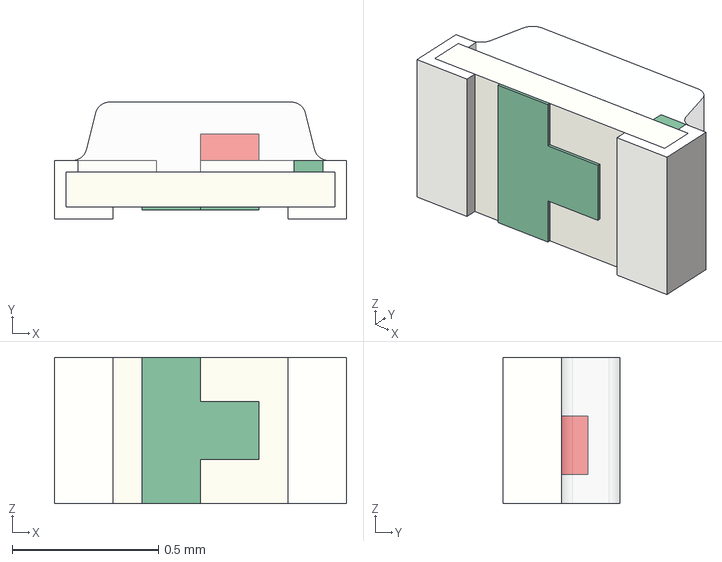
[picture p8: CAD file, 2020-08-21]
pcb/components/BL-HUB37A-AV-TRB/BL-HUB37A-AV-TRB.stp
1.00 x 0.4 x 0.5 mm

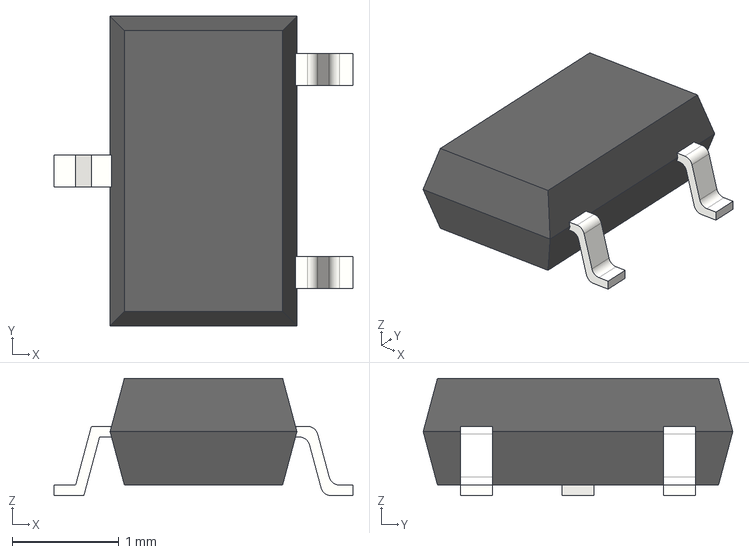
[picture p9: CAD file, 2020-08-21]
pcb/components/BSS123L/SOT-23-3.stp
2.80 x 2.90 x 1.10 mm

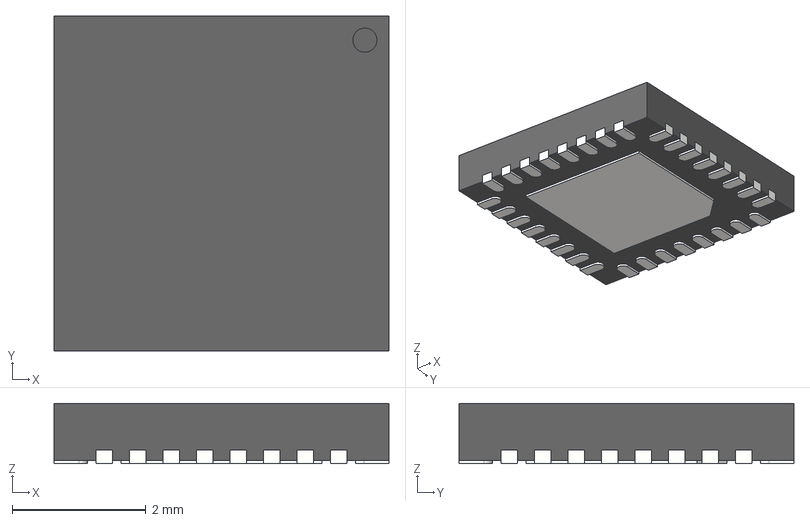
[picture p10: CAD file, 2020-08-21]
pcb/components/ICE40-LP384/ICE40-LP384-QFN32.stp
5.00 x 5.00 x 0.9 mm

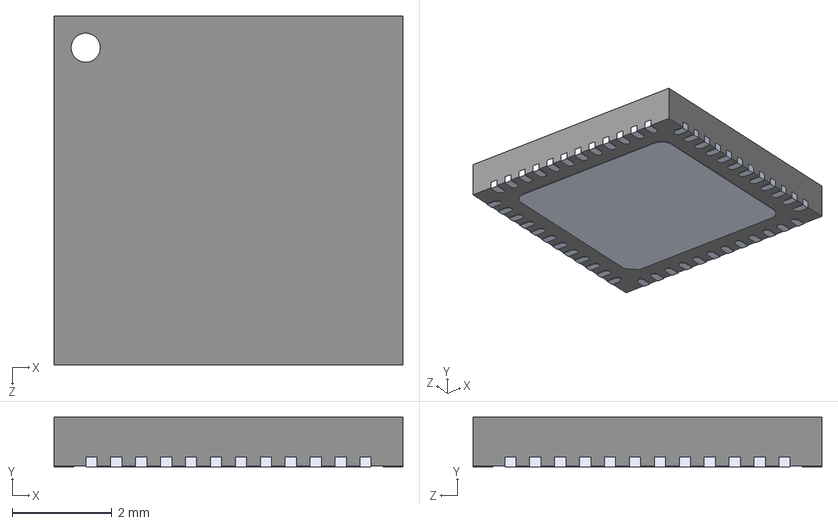
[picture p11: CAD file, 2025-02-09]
pcb/components/ICE40-UP5K/ICE40-UP5K-SG48I.STEP
7.00 x 1.00 x 7.00 mm

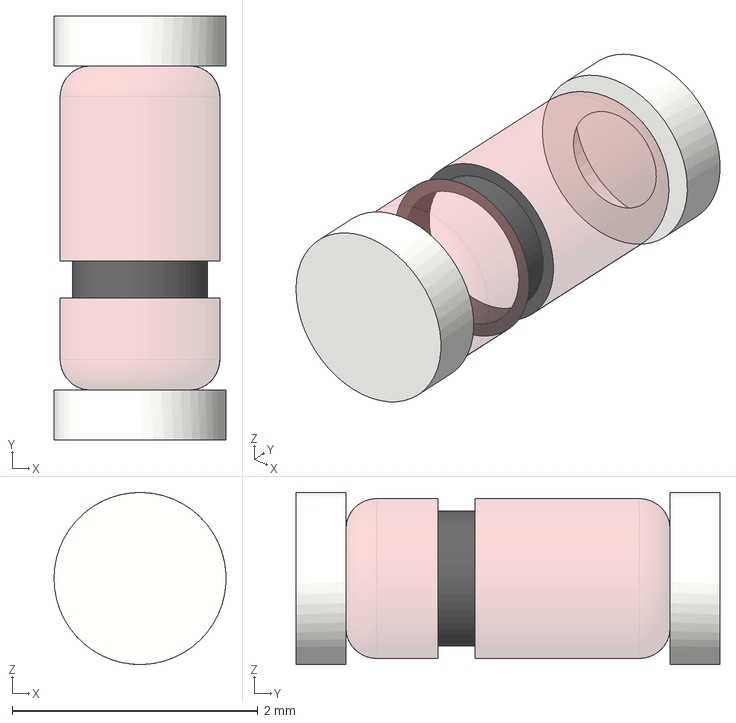
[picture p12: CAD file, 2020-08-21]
pcb/components/LL4148/SOD-80.stp
1.40 x 3.45 x 1.40 mm

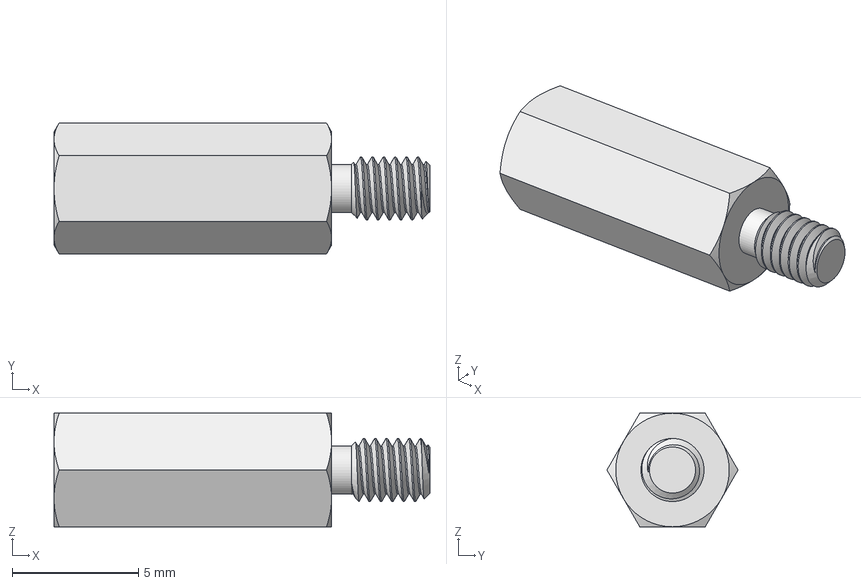
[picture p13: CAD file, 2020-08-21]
pcb/components/M2.5/M2.5x11-Standoff.stp
14.9 x 5.20 x 4.50 mm

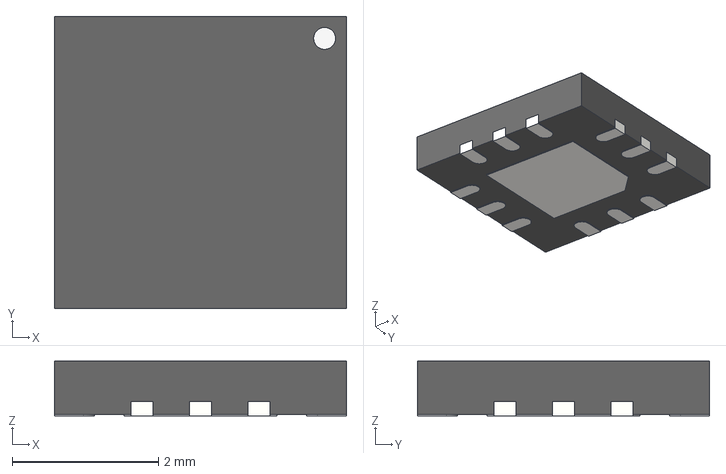
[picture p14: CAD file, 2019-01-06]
pcb/components/MAX1932/TQFN-12.stp
4.00 x 4.00 x 0.75 mm

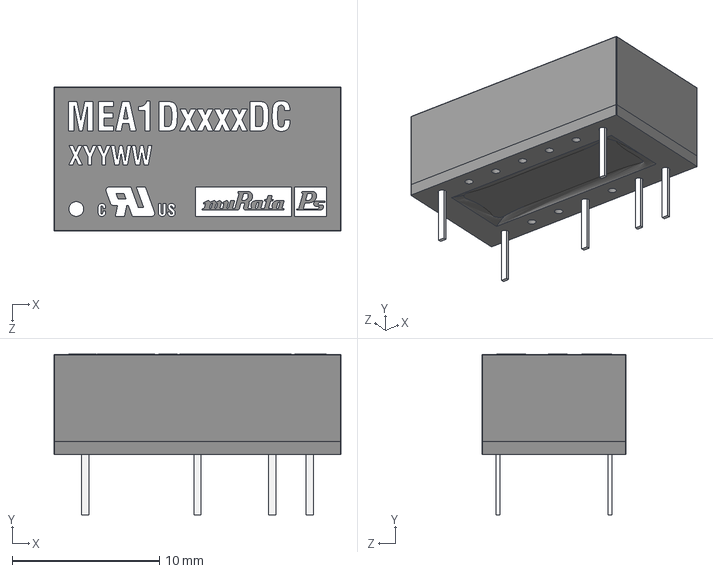
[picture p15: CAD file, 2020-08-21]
pcb/components/MEA1/MEA1-D.step
19.5 x 10.9 x 9.80 mm

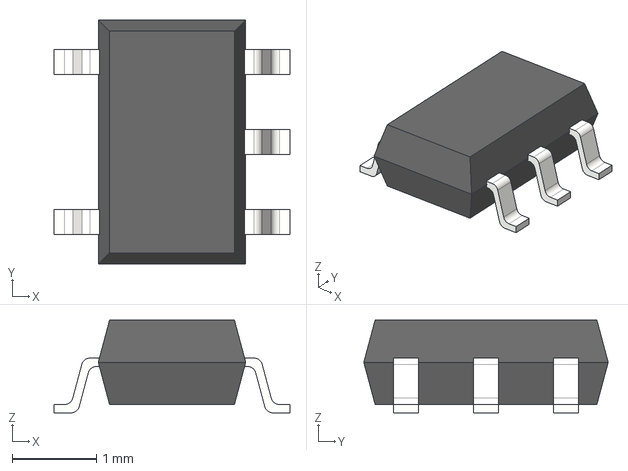
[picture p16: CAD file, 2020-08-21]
pcb/components/MIC550X/SOT-23-5.stp
2.80 x 2.90 x 1.10 mm

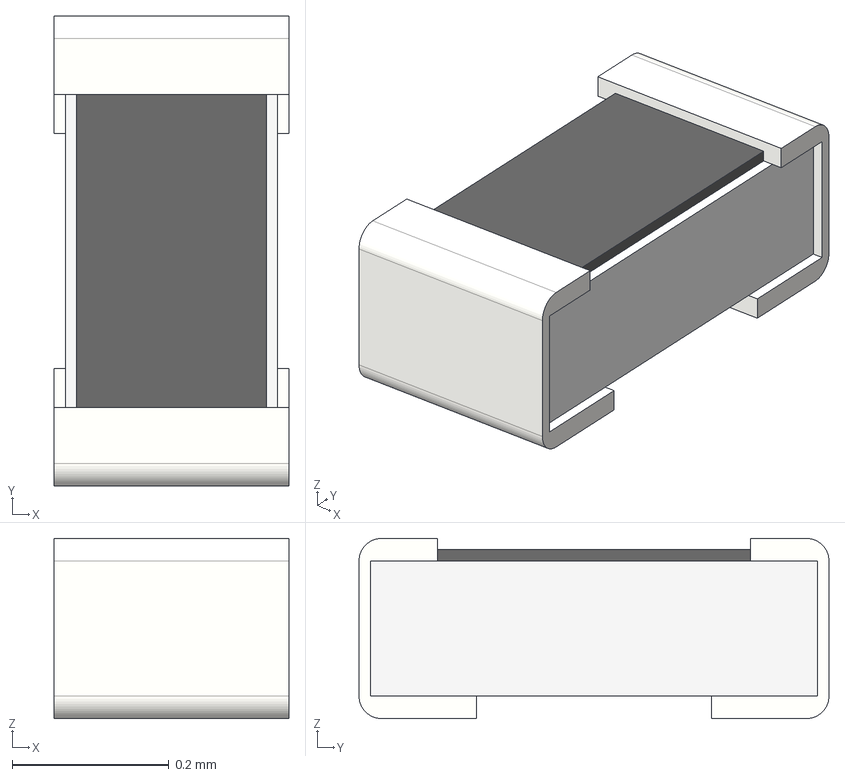
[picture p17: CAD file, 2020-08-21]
pcb/components/passives/R-0201.stp
0.3 x 0.6 x 0.23 mm

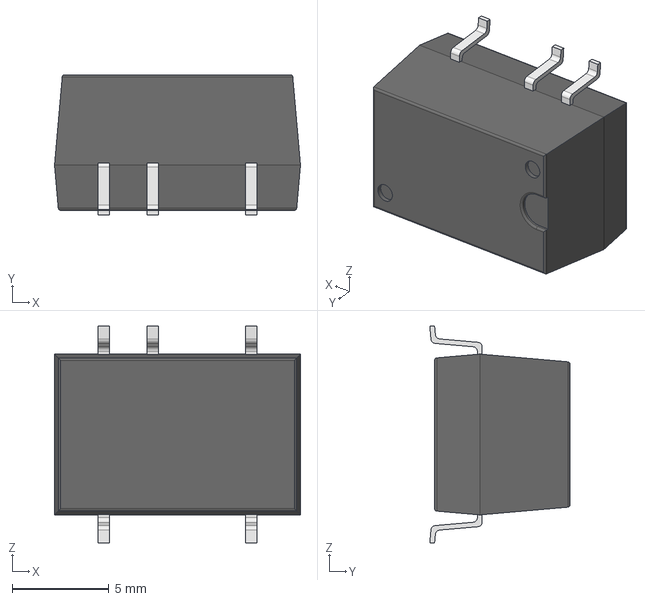
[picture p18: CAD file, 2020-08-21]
pcb/components/PDS1-M/PDS1-S-M.stp
12.7 x 7.25 x 11.2 mm

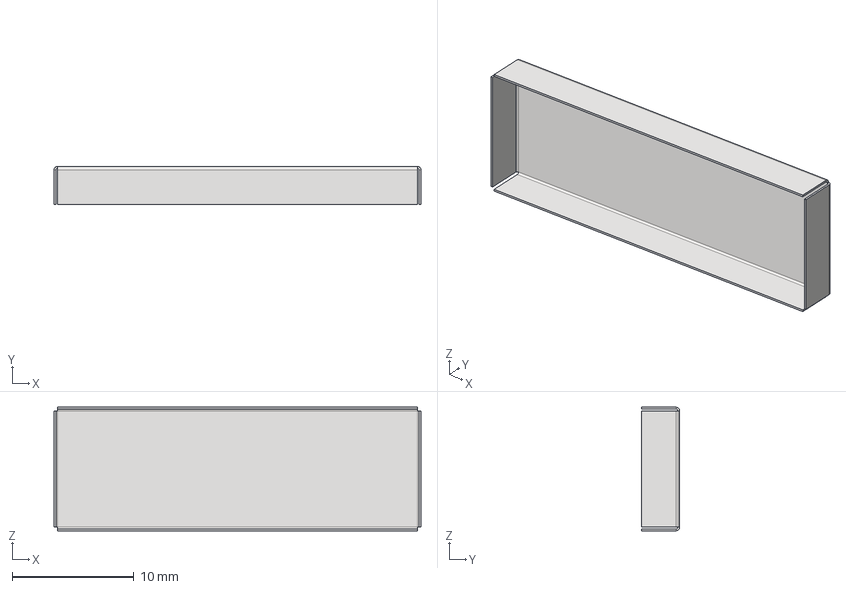
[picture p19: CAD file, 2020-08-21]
pcb/components/S03-XXXXXXX0R/S03-30100300R.stp
30.1 x 3.15 x 10.2 mm

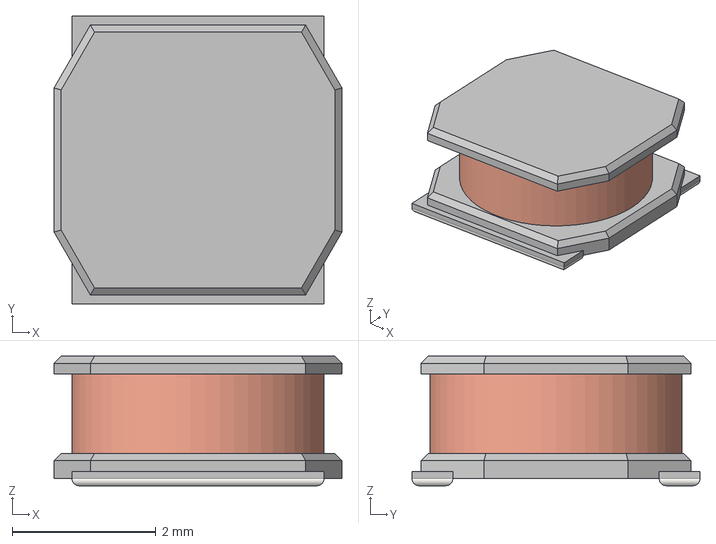
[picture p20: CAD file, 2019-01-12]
pcb/components/SRN4018/SRN4018.stp
4.00 x 4.00 x 1.80 mm

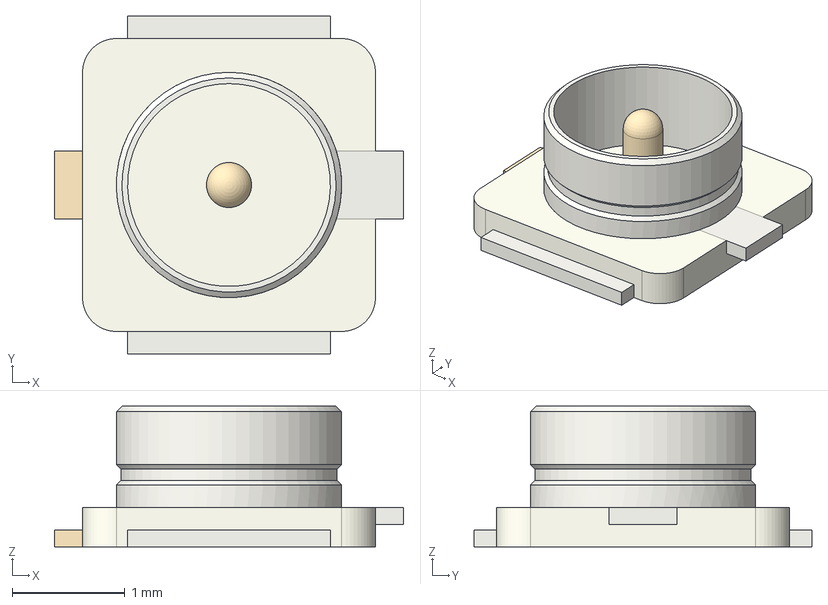
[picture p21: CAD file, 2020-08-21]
pcb/components/U.FL/U.FL 2.step
3.10 x 3.00 x 1.25 mm

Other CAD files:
pcb/components/passives/L-0402.stp
pcb/components/PDS1-M/PDS1-D-M.stp
pcb/components/passives/L-1210.stp
cad/mppcInterface.iam
pcb/components/DAC80508/DAC805008-RTE.stp
pcb/components/RaspberryPi/C35165.stp
pcb/components/S13360-2050VE/S13360-2050VE 2.stp
pcb/components/passives/C-0201.stp
pcb/components/passives/C-0402.stp
pcb/components/passives/C-0603.stp
pcb/components/passives/C-0805.stp
pcb/components/passives/C-1206.stp
pcb/components/passives/C-1210.stp
pcb/components/passives/C-1812.stp
pcb/components/passives/C-2220.stp
pcb/components/passives/L-0603.stp
pcb/components/passives/L-0805.stp
pcb/components/passives/L-1206.stp
pcb/components/passives/R-0402.stp
pcb/components/passives/R-0603.stp
pcb/components/passives/R-0805.stp
pcb/components/passives/R-1206.stp

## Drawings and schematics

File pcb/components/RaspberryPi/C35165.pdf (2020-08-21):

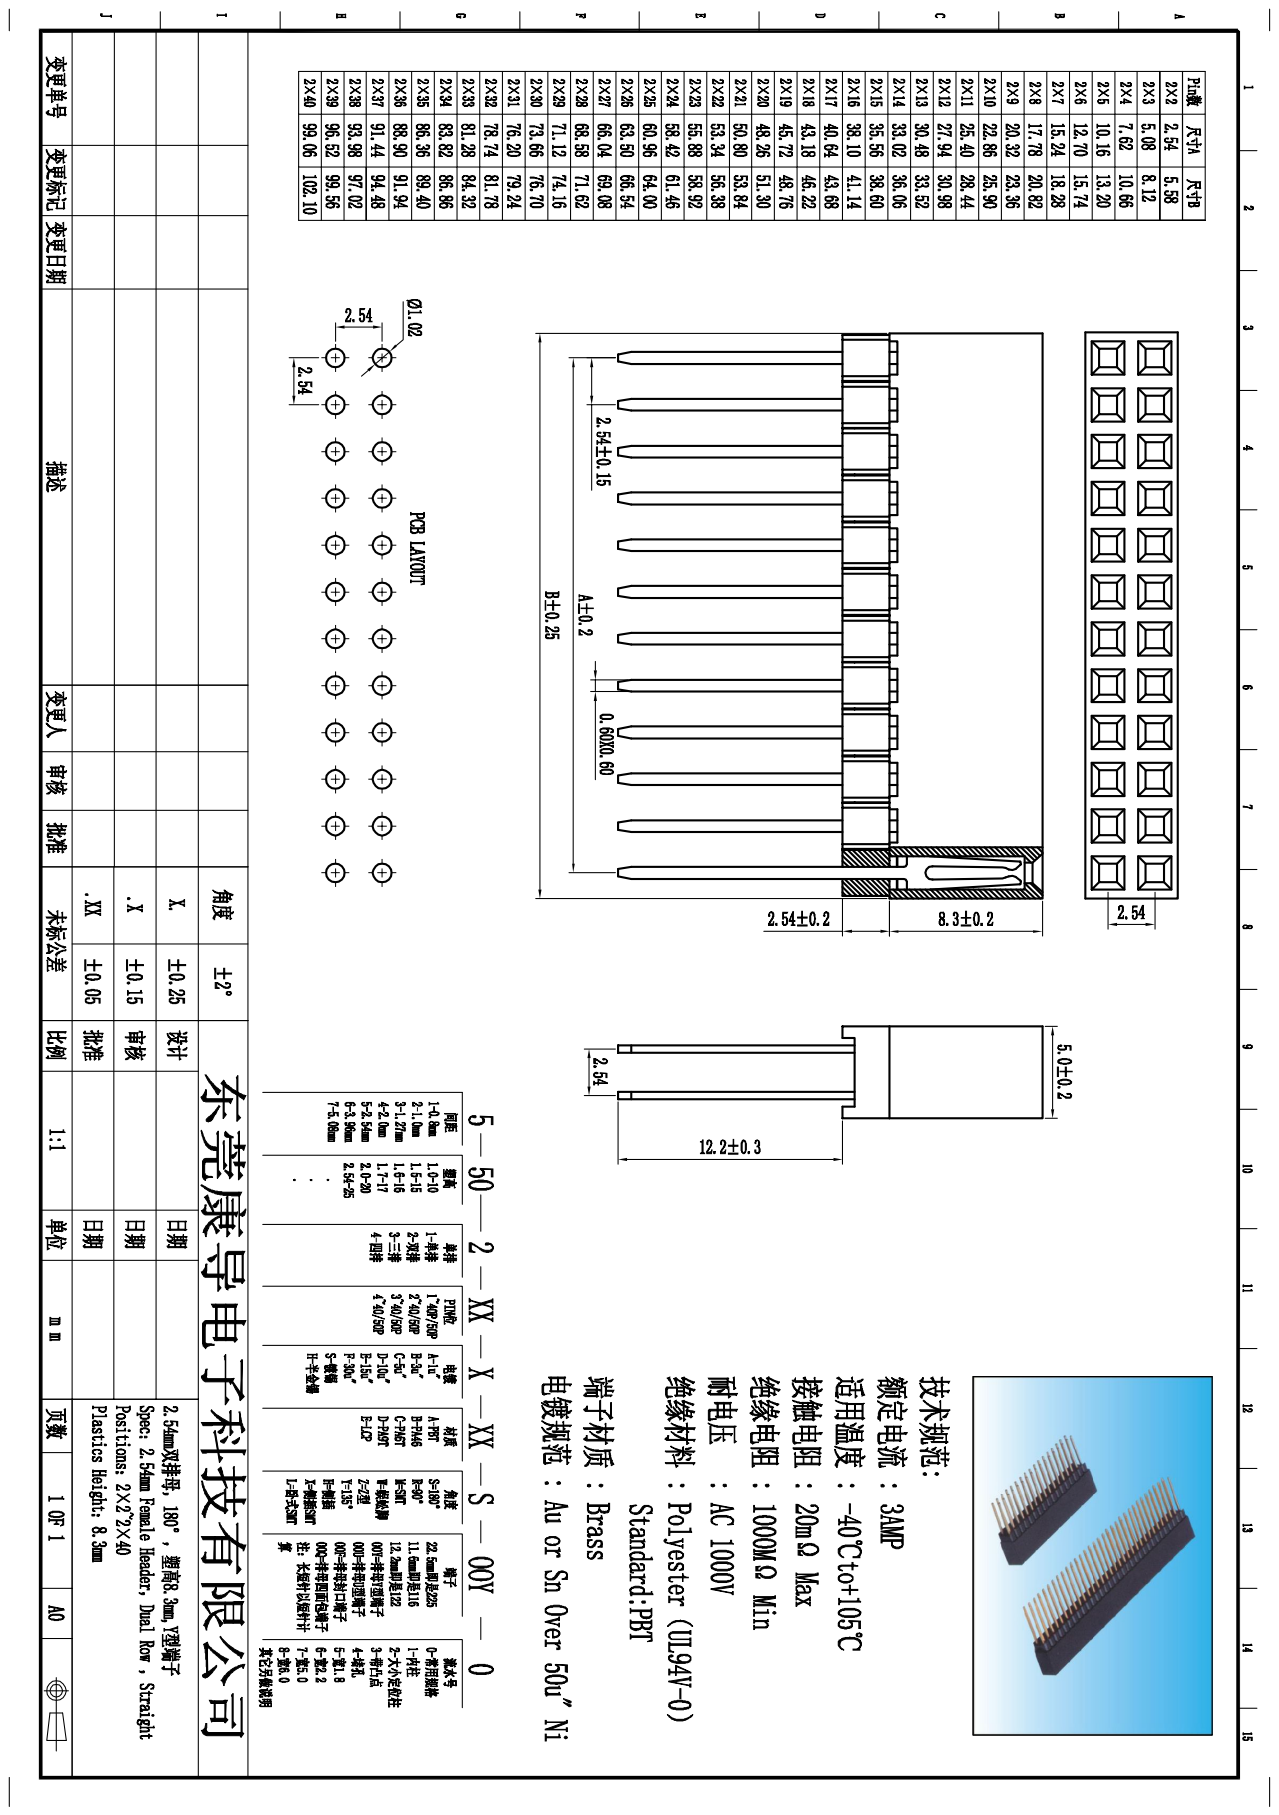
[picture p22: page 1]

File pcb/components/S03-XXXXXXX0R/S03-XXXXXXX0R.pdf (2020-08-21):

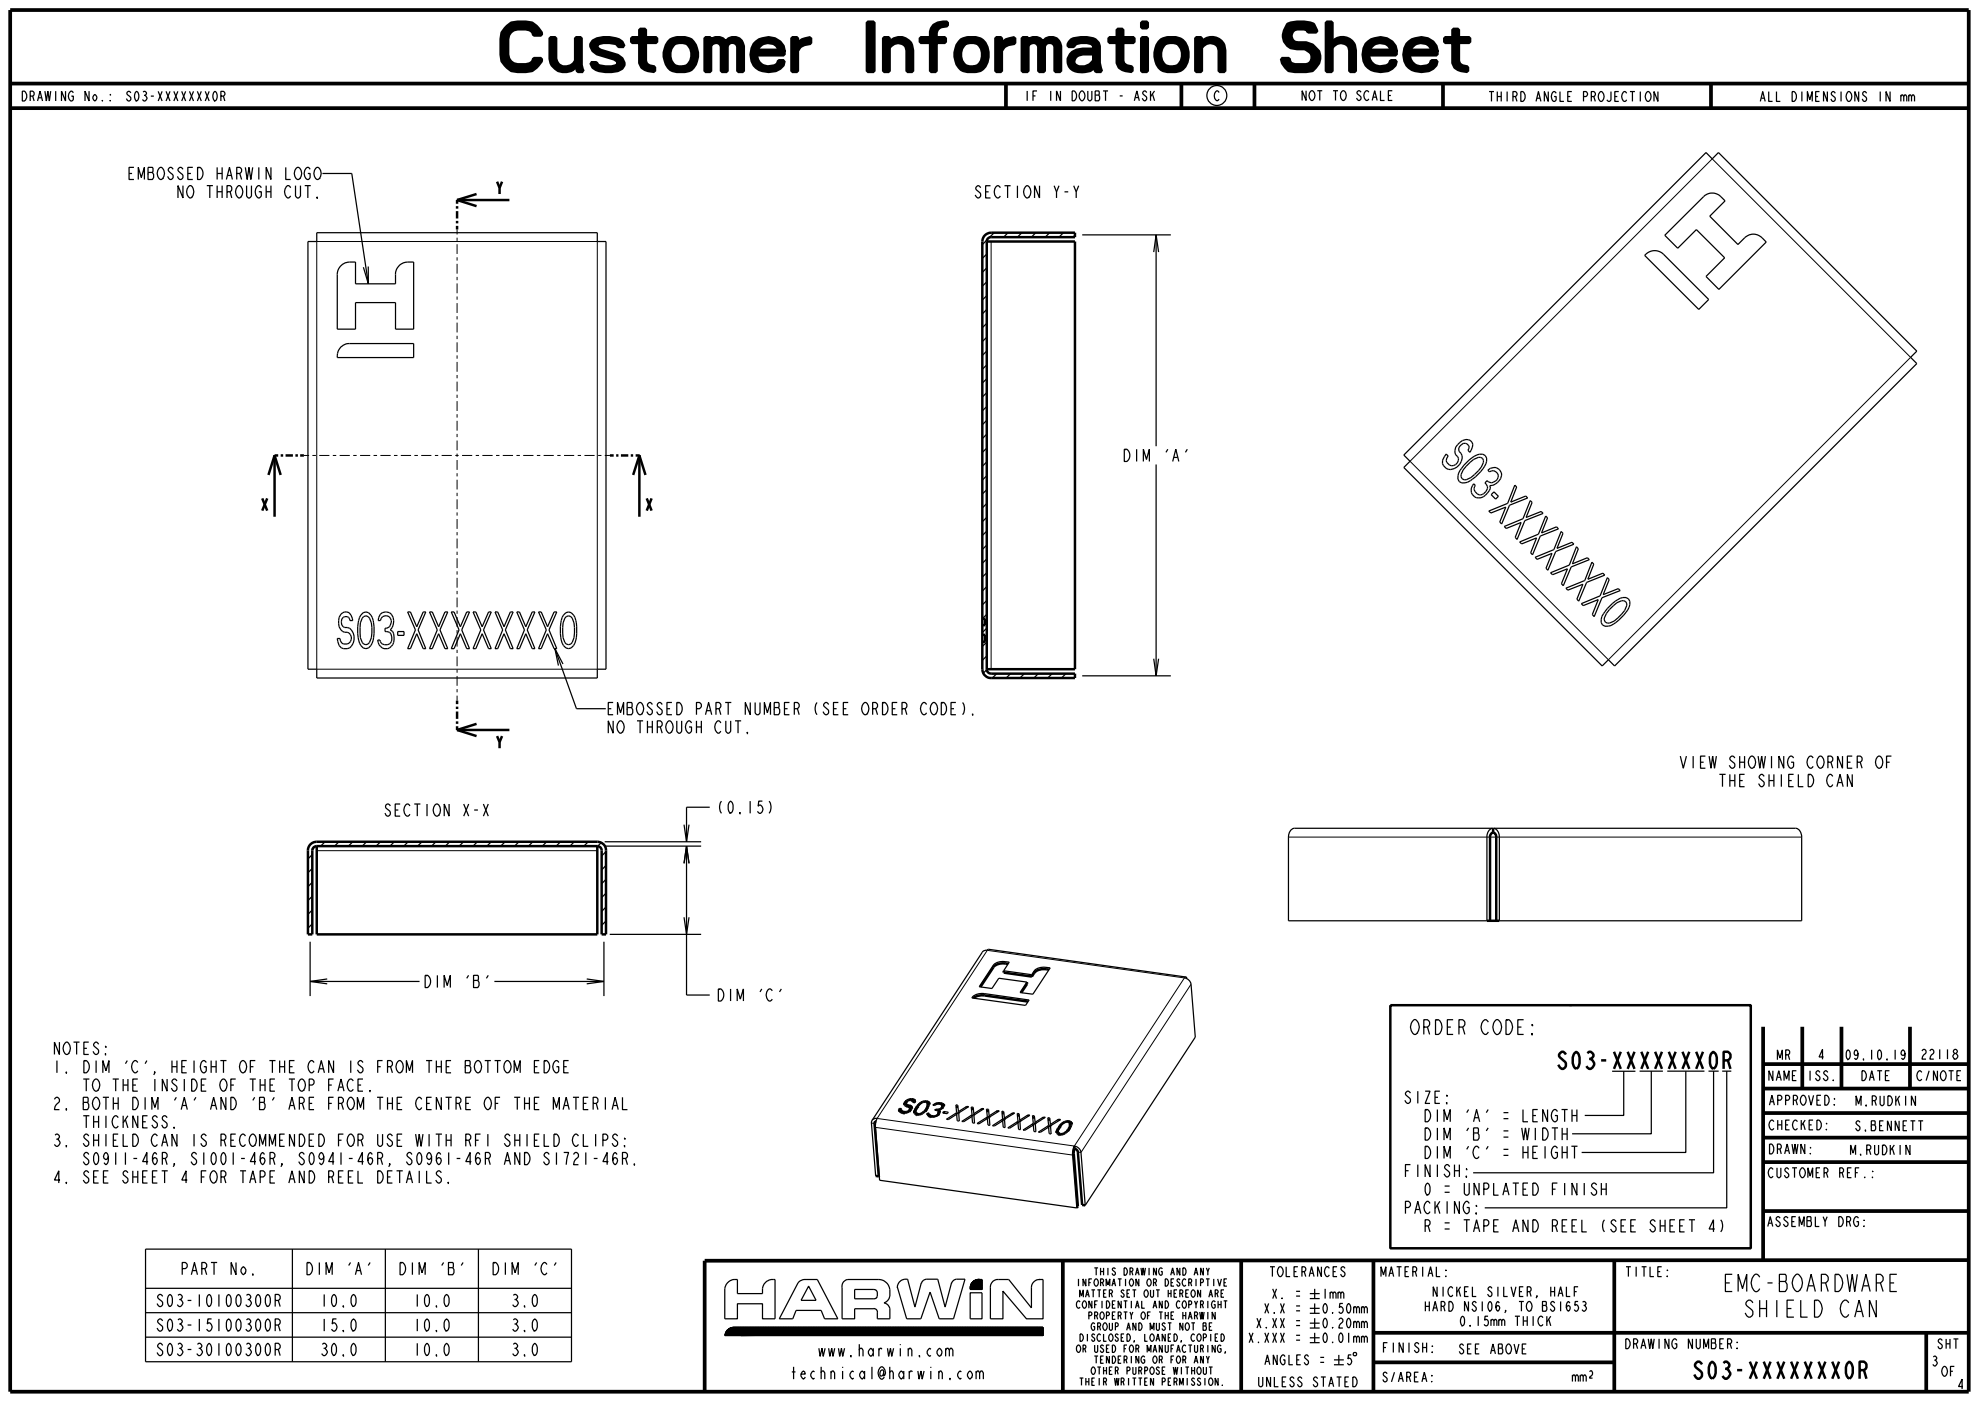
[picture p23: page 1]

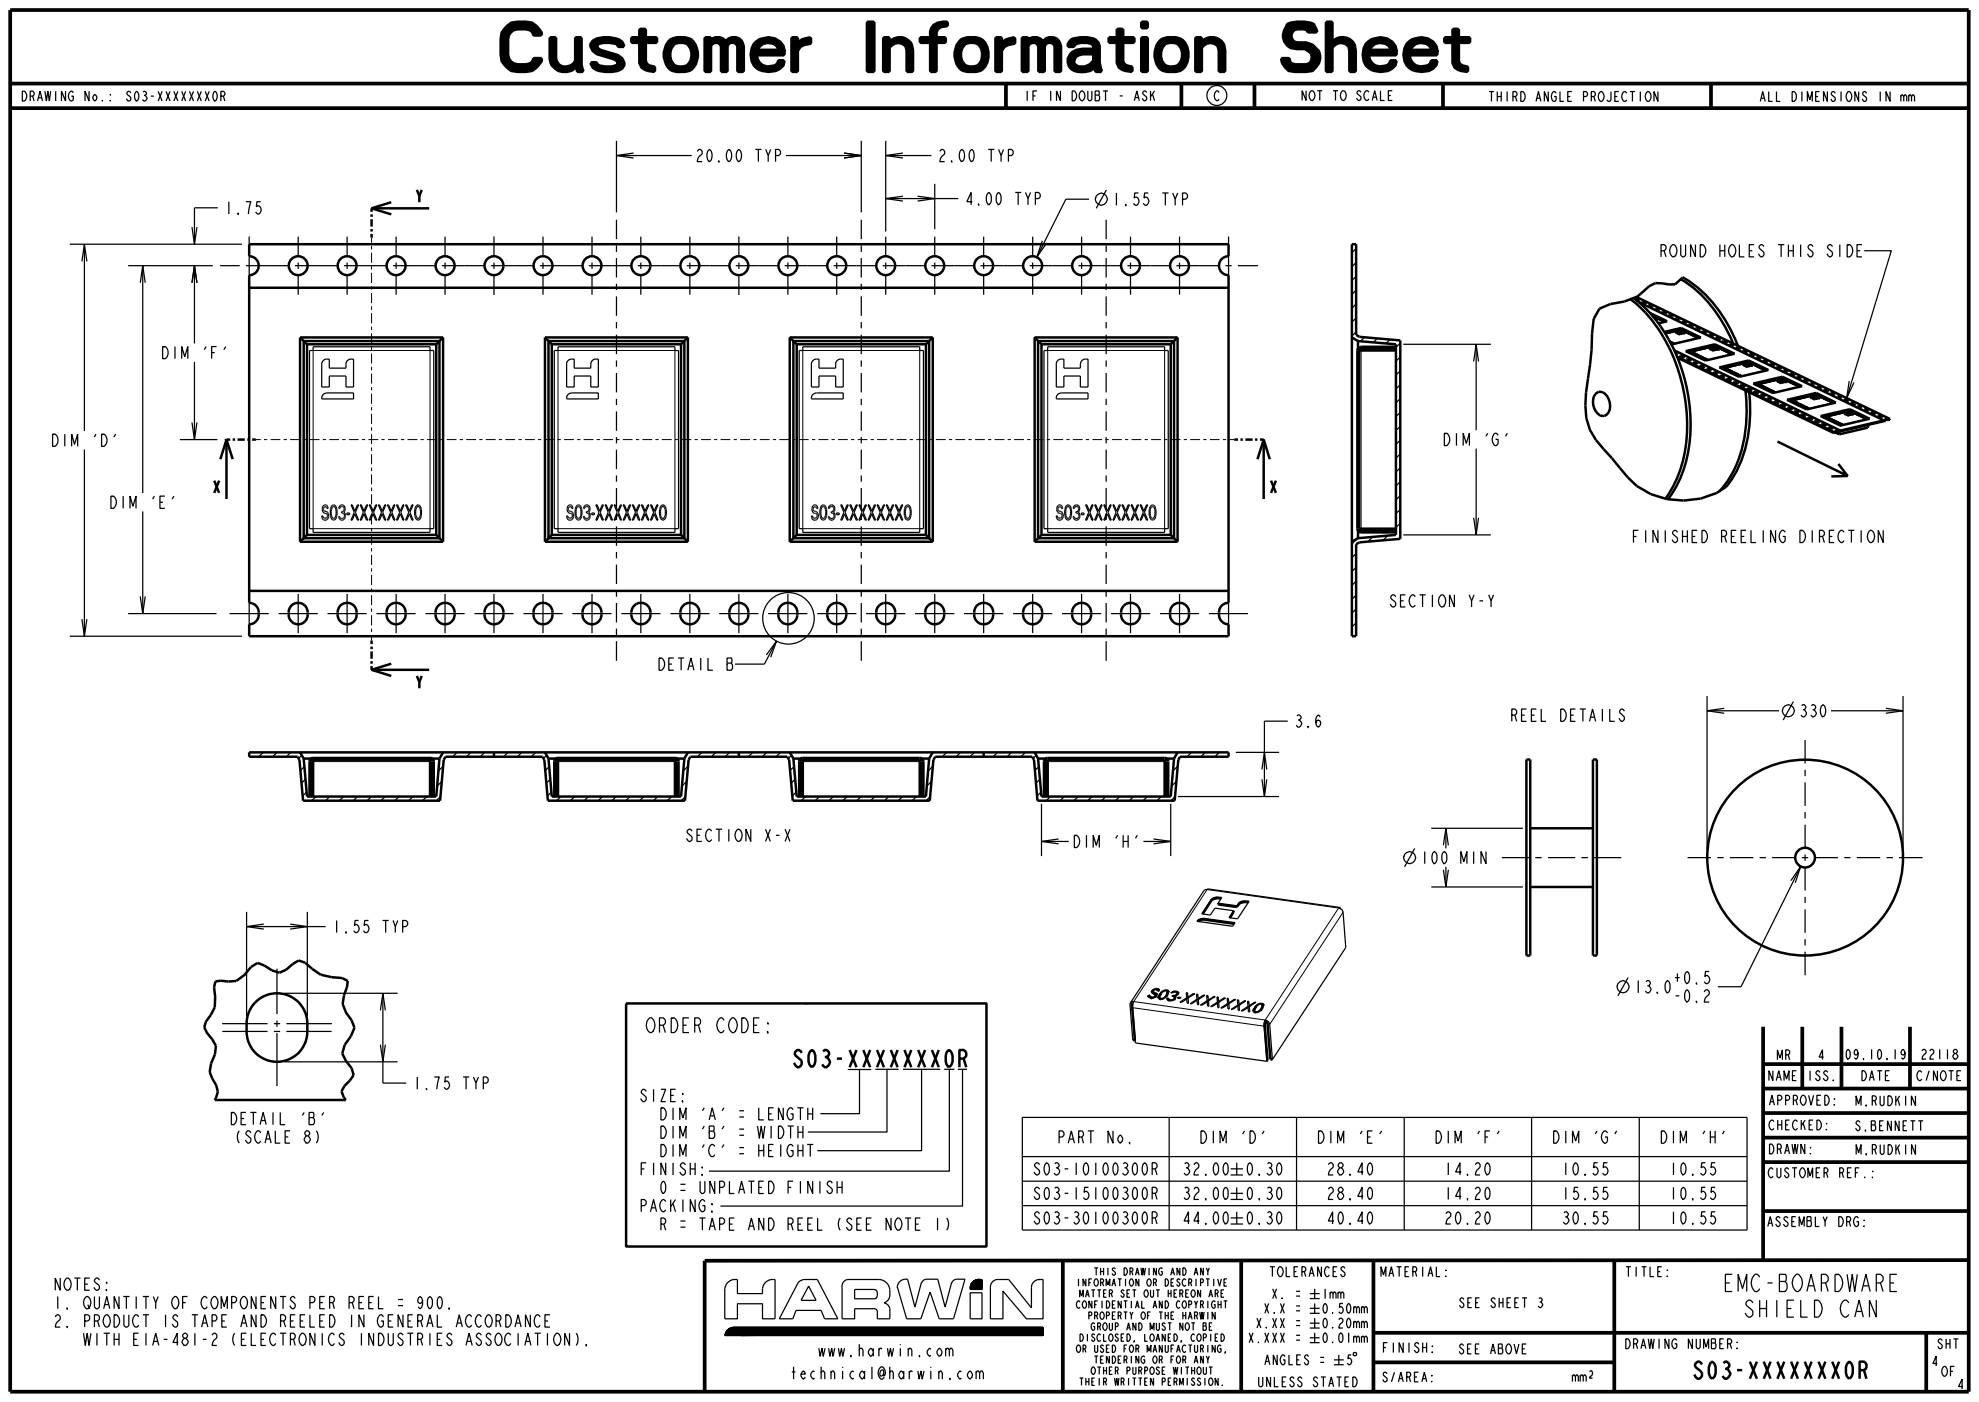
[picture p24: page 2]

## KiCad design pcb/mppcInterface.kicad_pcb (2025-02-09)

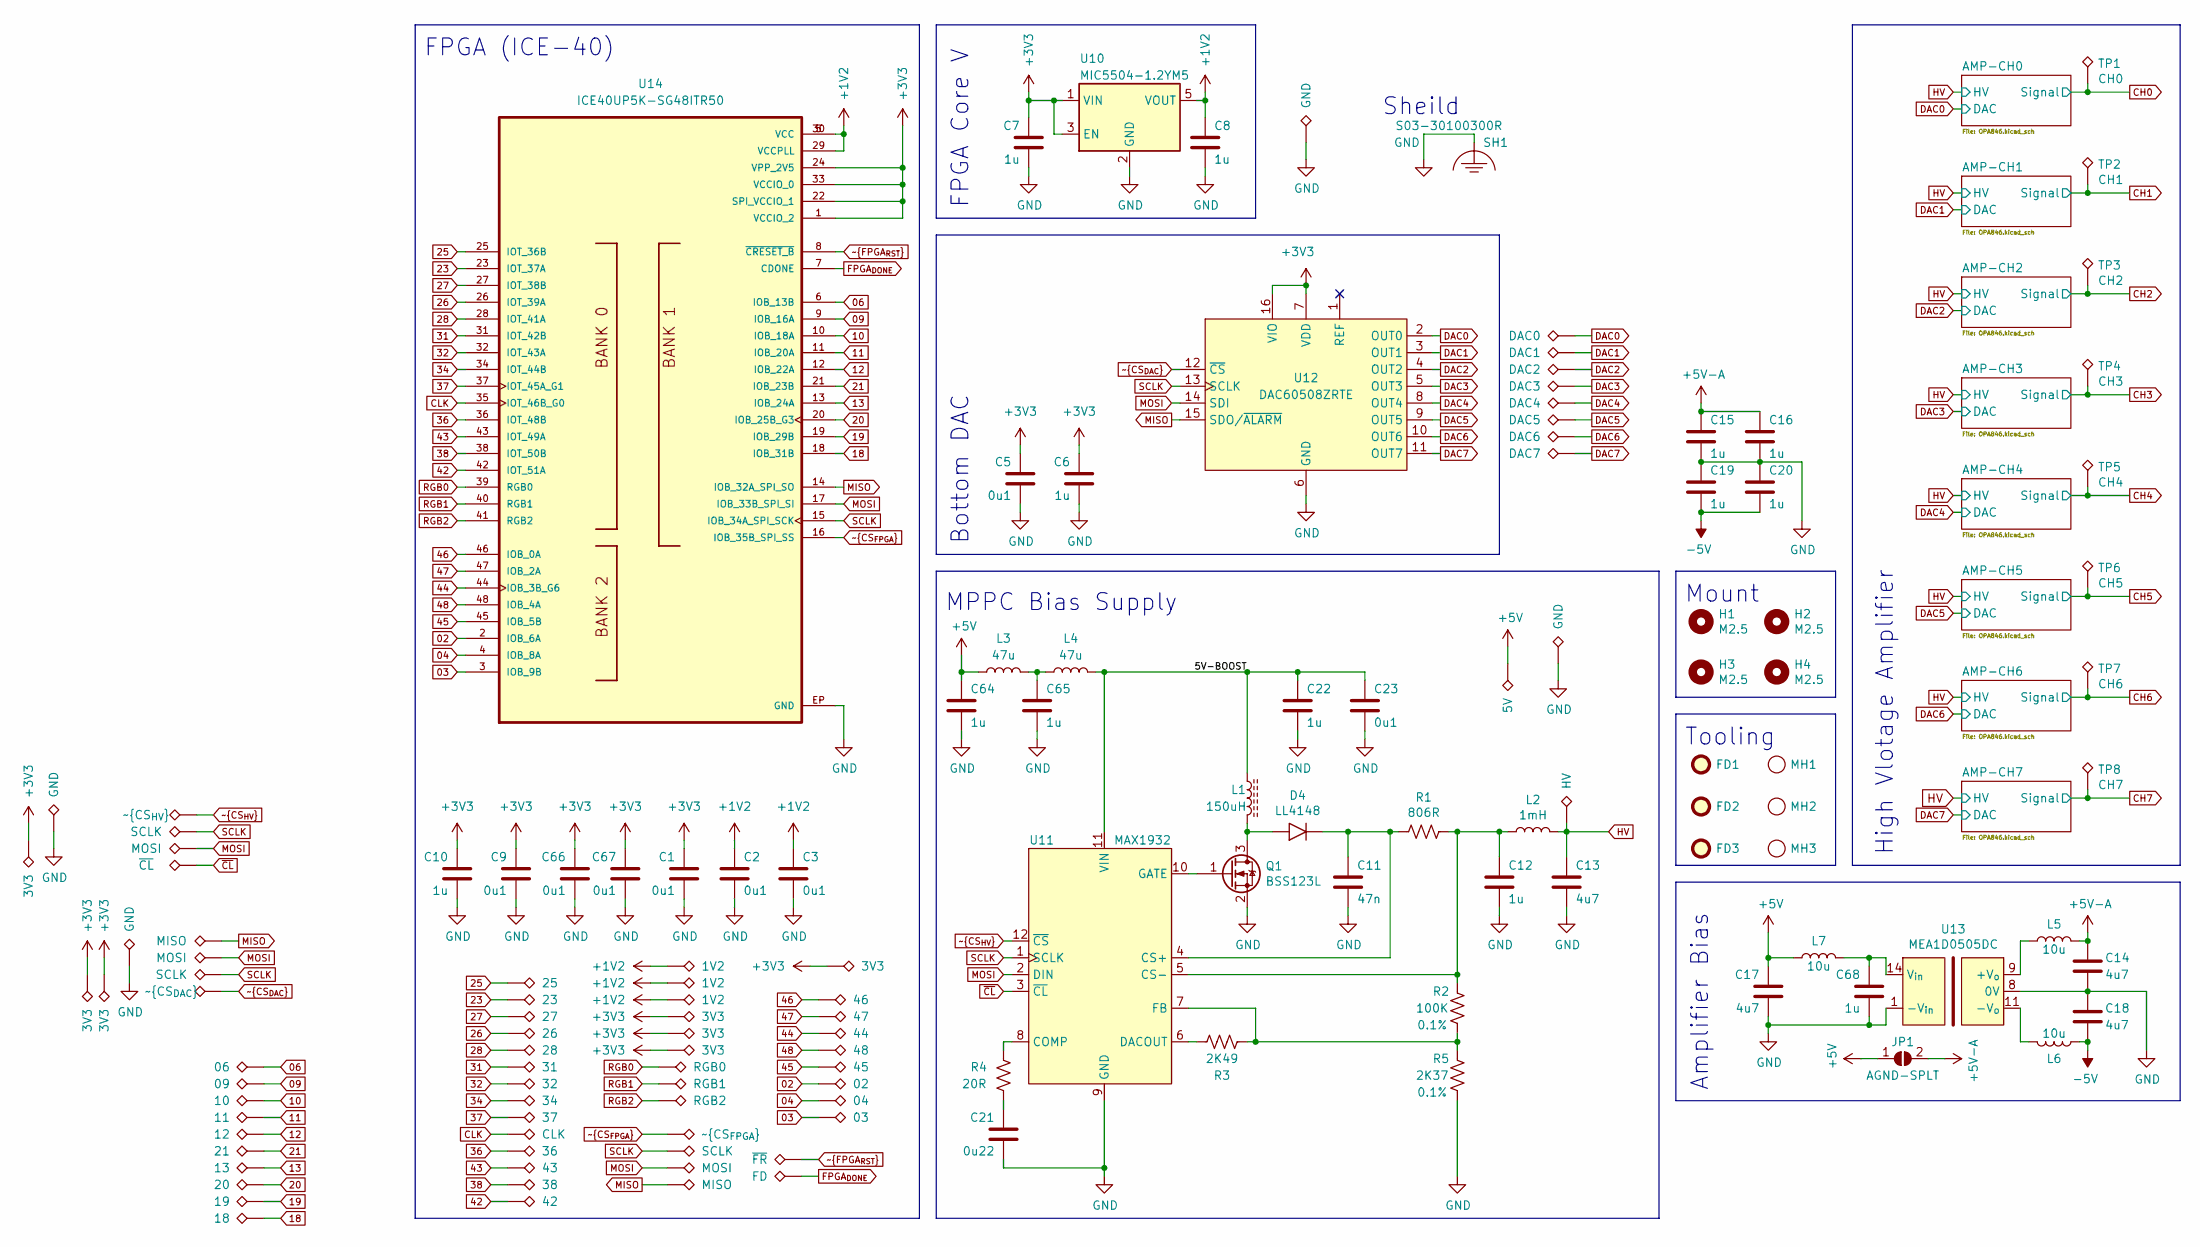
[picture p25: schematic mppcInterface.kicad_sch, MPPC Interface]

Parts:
C1, C2, C3, C5, C9, C23, C66, C67: 0u1; C-0402
C6, C7, C8, C10, C15, C16, C19, C20, C22: 1u; C-0402
C11: 47n; C-0805
C12: 1u; C-1206
C13: 4u7; C-2220
C14, C17, C18: 4u7; C-0805
C21: 0u22; C-0402
C64, C65, C68: 1u; C-0805
D4: LL4148; SOD-80
FD1, FD2, FD3: Fiducial; Fiducial_1.5mm_Mask3mm
H1, H2, H3, H4: M2.5; M2.5x11-Standoff
JP1: AGND-SPLT; SolderJumper-2_P1.3mm_Open_RoundedPad1.0x1.5mm
L1: 150uH; SRN4018
L2: 1mH; L-1210
L3, L4: 47u; L-0805
L5, L6, L7: 10u; L-0805
MH1, MH2, MH3: toolingHole; 1.152mm-ToolingHole
Q1: BSS123L; SOT-23-3
R1: 806R; R-0402
R2: 100K; R-0402; Tolerance 0.1%
R3: 2K49; R-0402
R4: 20R; R-0402
R5: 2K37; R-0402; Tolerance 0.1%
SH1: S03-30100300R
TP1: CH0; TestPoint_Pad_D1.0mm
TP2: CH1; TestPoint_Pad_D1.0mm
TP3: CH2; TestPoint_Pad_D1.0mm
TP4: CH3; TestPoint_Pad_D1.0mm
TP5: CH4; TestPoint_Pad_D1.0mm
TP6: CH5; TestPoint_Pad_D1.0mm
TP7: CH6; TestPoint_Pad_D1.0mm
TP8: CH7; TestPoint_Pad_D1.0mm
TP9: 5V; 0.1in Pin
TP11: 25; 0.1in Pin
TP12: 23; 0.1in Pin
TP13: 27; 0.1in Pin
TP14: 26; 0.1in Pin
TP15: 28; 0.1in Pin
TP16: 31; 0.1in Pin
TP17: 32; 0.1in Pin
TP18: 34; 0.1in Pin
TP19: 37; 0.1in Pin
TP20: CLK; 0.1in Pin
TP21: 36; 0.1in Pin
TP22: 43; 0.1in Pin
TP23: 38; 0.1in Pin
TP24: 42; 0.1in Pin
TP25, TP26, TP64: 1V2; 0.1in Pin
TP27, TP28, TP65, TP66, TP77, TP78, TP80: 3V3; 0.1in Pin
TP29: DAC3; 0.1in Pin
TP30: DAC2; 0.1in Pin
TP31: DAC1; 0.1in Pin
TP32: DAC0; 0.1in Pin
TP33: DAC4; 0.1in Pin
TP34: DAC5; 0.1in Pin
TP35: DAC6; 0.1in Pin
TP36: DAC7; 0.1in Pin
TP37: RGB0; 0.1in Pin
TP38: RGB1; 0.1in Pin
TP39: RGB2; 0.1in Pin
TP40: 46; 0.1in Pin
TP41: 47; 0.1in Pin
TP42: 44; 0.1in Pin
TP43: 48; 0.1in Pin
TP44: 45; 0.1in Pin
TP45: 02; 0.1in Pin
TP46: 04; 0.1in Pin
TP47: 03; 0.1in Pin
TP48: ~{CS_{FPGA}}; 0.1in Pin
TP49, TP70, TP73: SCLK; 0.1in Pin
TP50, TP69, TP74: MOSI; 0.1in Pin
TP51, TP68: MISO; 0.1in Pin
TP52: 06; 0.1in Pin
TP53: 09; 0.1in Pin
TP54: 10; 0.1in Pin
TP55: 11; 0.1in Pin
TP56: 12; 0.1in Pin
TP57: 21; 0.1in Pin
TP58: 13; 0.1in Pin
TP59: 20; 0.1in Pin
TP60: 19; 0.1in Pin
TP61: 18; 0.1in Pin
TP62: ~{FR}; 0.1in Pin
TP63: FD; 0.1in Pin
TP67, TP76, TP79, TP81: GND; 0.1in Pin
TP71: ~{CS_{DAC}}; 0.1in Pin
TP72: ~{CS_{HV}}; 0.1in Pin
TP75: ~{CL}; 0.1in Pin
TP82: HV; 0.1in Pin
U10: MIC5504-1.2YM5; SOT-23-5
U11: MAX1932; TQFN-12
U12: DAC60508ZRTE; DAC80508-RTE
U13: MEA1D0505DC; MEA1-D
U14: ICE40UP5K-SG48ITR50; ICE40-UP5K-SG48I; PARTREV 1.4

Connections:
02: TP45.1, U14.2 (IOB_6A)
03: TP47.1, U14.3 (IOB_9B)
04: TP46.1, U14.4 (IOB_8A)
06: TP52.1, U14.6 (IOB_13B)
09: TP53.1, U14.9 (IOB_16A)
10: TP54.1, U14.10 (IOB_18A)
11: TP55.1, U14.11 (IOB_20A)
12: TP56.1, U14.12 (IOB_22A)
13: TP58.1, U14.13 (IOB_24A)
18: TP61.1, U14.18 (IOB_31B)
19: TP60.1, U14.19 (IOB_29B)
20: TP59.1, U14.20 (IOB_25B_G3)
21: TP57.1, U14.21 (IOB_23B)
23: TP12.1, U14.23 (IOT_37A)
25: TP11.1, U14.25 (IOT_36B)
26: TP14.1, U14.26 (IOT_39A)
27: TP13.1, U14.27 (IOT_38B)
28: TP15.1, U14.28 (IOT_41A)
31: TP16.1, U14.31 (IOT_42B)
32: TP17.1, U14.32 (IOT_43A)
34: TP18.1, U14.34 (IOT_44B)
36: TP21.1, U14.36 (IOT_48B)
37: TP19.1, U14.37 (IOT_45A_G1)
38: TP23.1, U14.38 (IOT_50B)
42: TP24.1, U14.42 (IOT_51A)
43: TP22.1, U14.43 (IOT_49A)
44: TP42.1, U14.44 (IOB_3B_G6)
45: TP44.1, U14.45 (IOB_5B)
46: TP40.1, U14.46 (IOB_0A)
47: TP41.1, U14.47 (IOB_2A)
48: TP43.1, U14.48 (IOB_4A)
+1V2: C2.2, C3.2, C8.2, TP25.1, TP26.1, TP64.1, U10.5 (VOUT), U14.5 (VCC), U14.29 (VCCPLL), U14.30 (VCC)
+3V3: C1.2, C5.2, C6.2, C7.2, C9.2, C10.2, C66.2, C67.2, TP27.1, TP28.1, TP65.1, TP66.1, TP77.1, TP78.1, TP80.1, U10.1 (VIN), U10.3 (EN), U12.7 (VDD), U12.16 (VIO), U14.1 (VCCIO_2), U14.22 (SPI_VCCIO_1), U14.24 (VPP_2V5), U14.33 (VCCIO_0)
+5V: C17.1, C64.2, JP1.1 (A), L3.1, L7.1, TP9.1
+5V-A: C14.1, C15.2, C16.2, JP1.2 (B), L5.2; also elsewhere on the board
-5V: C18.2, C19.1, C20.1, L6.1; also elsewhere on the board
/5V-BOOST: C22.2, C23.1, L1.1, L4.2, U11.11 (VIN)
CH0: TP1.1; also elsewhere on the board
CH1: TP2.1; also elsewhere on the board
CH2: TP3.1; also elsewhere on the board
CH3: TP4.1; also elsewhere on the board
CH4: TP5.1; also elsewhere on the board
CH5: TP6.1; also elsewhere on the board
CH6: TP7.1; also elsewhere on the board
CH7: TP8.1; also elsewhere on the board
CLK: TP20.1, U14.35 (IOT_46B_G0)
DAC0: TP32.1, U12.2 (OUT0); also elsewhere on the board
DAC1: TP31.1, U12.3 (OUT1); also elsewhere on the board
DAC2: TP30.1, U12.4 (OUT2); also elsewhere on the board
DAC3: TP29.1, U12.5 (OUT3); also elsewhere on the board
DAC4: TP33.1, U12.8 (OUT4); also elsewhere on the board
DAC5: TP34.1, U12.9 (OUT5); also elsewhere on the board
DAC6: TP35.1, U12.10 (OUT6); also elsewhere on the board
DAC7: TP36.1, U12.11 (OUT7); also elsewhere on the board
FPGA_{DONE}: TP63.1, U14.7 (CDONE)
GND: C1.1, C2.1, C3.1, C5.1, C6.1, C7.1, C8.1, C9.1, C10.1, C11.2, C12.2, C13.2, C14.2, C15.1, C16.1, C17.2, C18.1, C19.2, C20.2, C21.2, C22.1, C23.2, C64.1, C65.1, C66.1, C67.1, C68.2, Q1.2 (S), R5.2, SH1.1 (SHIELD), TP67.1, TP76.1, TP79.1, TP81.1, U10.2 (GND), U11.9 (GND), U12.6 (GND), U13.1 (-V_{in}), U13.8 (0V), U14.EP (GND); also elsewhere on the board
HV: C13.1, L2.2, TP82.1; also elsewhere on the board
MISO: TP51.1, TP68.1, U12.15 (SDO/~ALARM), U14.14 (IOB_32A_SPI_SO)
MOSI: TP50.1, TP69.1, TP74.1, U11.2 (DIN), U12.14 (SDI), U14.17 (IOB_33B_SPI_SI)
unnamed: C21.1, R4.2
unnamed: C65.2, L3.2, L4.1
unnamed 69: D4.2 (A), L1.2, Q1.3 (D); also elsewhere on the board
unnamed 70: C11.1, D4.1 (K), R1.2, U11.4 (CS+); also elsewhere on the board
unnamed: Q1.1 (G), U11.10 (GATE)
unnamed: R4.1, U11.8 (COMP)
unnamed: C12.1, L2.1, R1.1, R2.1, U11.5 (CS-)
unnamed: R3.2, U11.6 (DACOUT)
unnamed: R2.2, R3.1, R5.1, U11.7 (FB)
unnamed: L5.1, U13.9 (+V_{o})
unnamed: L6.2, U13.11 (-V_{o})
unnamed: C68.1, L7.2, U13.14 (V_{in})
RGB0: TP37.1, U14.39 (RGB0)
RGB1: TP38.1, U14.40 (RGB1)
RGB2: TP39.1, U14.41 (RGB2)
SCLK: TP49.1, TP70.1, TP73.1, U11.1 (SCLK), U12.13 (SCLK), U14.15 (IOB_34A_SPI_SCK)
~CL: TP75.1, U11.3 (~CL)
~CS_{DAC}: TP71.1, U12.12 (~CS)
~CS_{FPGA}: TP48.1, U14.16 (IOB_35B_SPI_SS)
~CS_{HV}: TP72.1, U11.12 (~CS)
~FPGA_{RST}: TP62.1, U14.8 (~CRESET_B)

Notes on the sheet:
MPPC Bias Supply
Sheild
FPGA Core V
High Vlotage Amplifier
FPGA (ICE-40)
Tooling
Mount
Bottom DAC
Amplifier Bias

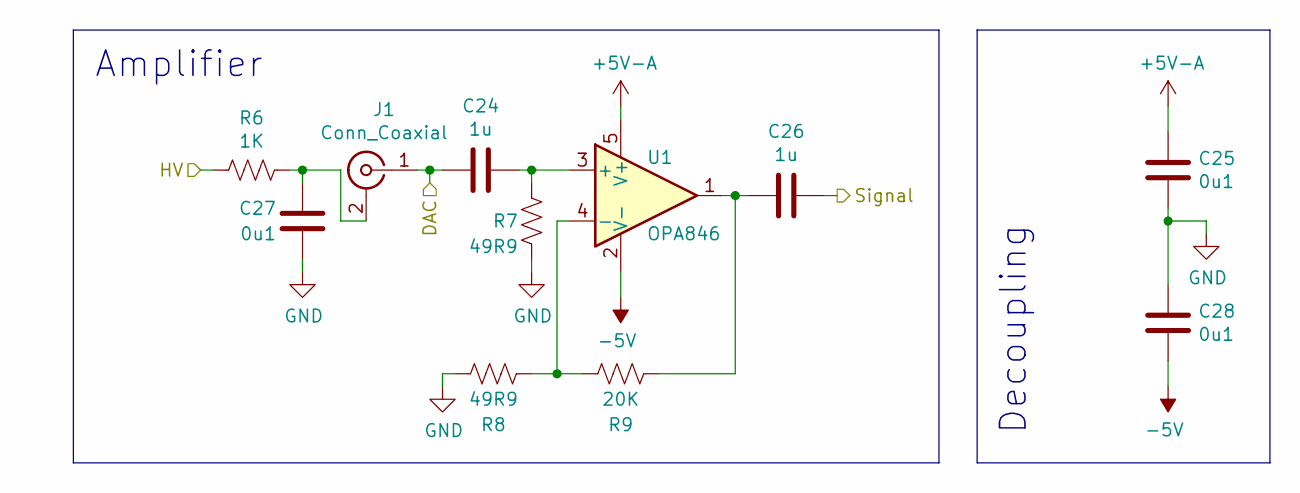
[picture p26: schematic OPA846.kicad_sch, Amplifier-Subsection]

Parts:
C24, C26: 1u; C-0402
C25, C27, C28: 0u1; C-0402
J1: Conn_Coaxial; U.FL
R6: 1K; R-0402
R7, R8: 49R9; R-0402
R9: 20K; R-0402
U1: OPA846; SOT-23-5

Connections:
+5V-A: C25.1, U1.5 (V+); also elsewhere on the board
-5V: C28.2, U1.2 (V-); also elsewhere on the board
CH0: C26.1; also elsewhere on the board
DAC0: C24.2, J1.1 (In); also elsewhere on the board
GND: C25.2, C27.2, C28.1, R7.1, R8.1; also elsewhere on the board
HV: R6.2; also elsewhere on the board
unnamed: C26.2, R9.1, U1.1
unnamed: C27.1, J1.2 (Ext), R6.1
unnamed: C24.1, R7.2, U1.3 (+)
unnamed: R8.2, R9.2, U1.4 (-)

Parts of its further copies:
C29, C31, C34, C36, C39, C41, C44, C46, C49, C51, C54, C56, C59, C61: 1u; C-0402
C30, C32, C33, C35, C37, C38, C40, C42, C43, C45, C47, C48, C50, C52, C53, C55, C57, C58, C60, C62, C63: 0u1; C-0402
J2, J3, J4, J5, J6, J7, J8: Conn_Coaxial; U.FL
R10, R14, R18, R22, R26, R30, R34: 1K; R-0402
R11, R12, R15, R16, R19, R20, R23, R24, R27, R28, R31, R32, R35, R36: 49R9; R-0402
R13, R17, R21, R25, R29, R33, R37: 20K; R-0402
U2, U3, U4, U5, U6, U7, U8: OPA846; SOT-23-5

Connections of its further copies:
+5V-A: C30.1, C35.1, C40.1, C45.1, C50.1, C55.1, C60.1, U2.5 (V+), U3.5 (V+), U4.5 (V+), U5.5 (V+), U6.5 (V+), U7.5 (V+), U8.5 (V+); also elsewhere on the board
-5V: C33.2, C38.2, C43.2, C48.2, C53.2, C58.2, C63.2, U2.2 (V-), U3.2 (V-), U4.2 (V-), U5.2 (V-), U6.2 (V-), U7.2 (V-), U8.2 (V-); also elsewhere on the board
CH1: C31.1; also elsewhere on the board
CH2: C36.1; also elsewhere on the board
CH3: C41.1; also elsewhere on the board
CH4: C46.1; also elsewhere on the board
CH5: C51.1; also elsewhere on the board
CH6: C56.1; also elsewhere on the board
CH7: C61.1; also elsewhere on the board
DAC1: C29.2, J2.1 (In); also elsewhere on the board
DAC2: C34.2, J3.1 (In); also elsewhere on the board
DAC3: C39.2, J4.1 (In); also elsewhere on the board
DAC4: C44.2, J5.1 (In); also elsewhere on the board
DAC5: C49.2, J6.1 (In); also elsewhere on the board
DAC6: C54.2, J7.1 (In); also elsewhere on the board
DAC7: C59.2, J8.1 (In); also elsewhere on the board
GND: C30.2, C32.2, C33.1, C35.2, C37.2, C38.1, C40.2, C42.2, C43.1, C45.2, C47.2, C48.1, C50.2, C52.2, C53.1, C55.2, C57.2, C58.1, C60.2, C62.2, C63.1, R11.1, R12.1, R15.1, R16.1, R19.1, R20.1, R23.1, R24.1, R27.1, R28.1, R31.1, R32.1, R35.1, R36.1; also elsewhere on the board
HV: R10.2, R14.2, R18.2, R22.2, R26.2, R30.2, R34.2; also elsewhere on the board
unnamed: C31.2, R13.1, U2.1
unnamed: C36.2, R17.1, U3.1
unnamed: C41.2, R21.1, U4.1
unnamed: C46.2, R25.1, U5.1
unnamed: C51.2, R29.1, U6.1
unnamed: C56.2, R33.1, U7.1
unnamed: C61.2, R37.1, U8.1
unnamed: C32.1, J2.2 (Ext), R10.1
unnamed: C37.1, J3.2 (Ext), R14.1
unnamed: C42.1, J4.2 (Ext), R18.1
unnamed: C47.1, J5.2 (Ext), R22.1
unnamed: C52.1, J6.2 (Ext), R26.1
unnamed: C57.1, J7.2 (Ext), R30.1
unnamed: C62.1, J8.2 (Ext), R34.1
unnamed: C29.1, R11.2, U2.3 (+)
unnamed: R12.2, R13.2, U2.4 (-)
unnamed: C34.1, R15.2, U3.3 (+)
unnamed: R16.2, R17.2, U3.4 (-)
unnamed: C39.1, R19.2, U4.3 (+)
unnamed: R20.2, R21.2, U4.4 (-)
unnamed: C44.1, R23.2, U5.3 (+)
unnamed: R24.2, R25.2, U5.4 (-)
unnamed: C49.1, R27.2, U6.3 (+)
unnamed: R28.2, R29.2, U6.4 (-)
unnamed: C54.1, R31.2, U7.3 (+)
unnamed: R32.2, R33.2, U7.4 (-)
unnamed: C59.1, R35.2, U8.3 (+)
unnamed: R36.2, R37.2, U8.4 (-)

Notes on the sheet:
Amplifier
Decoupling

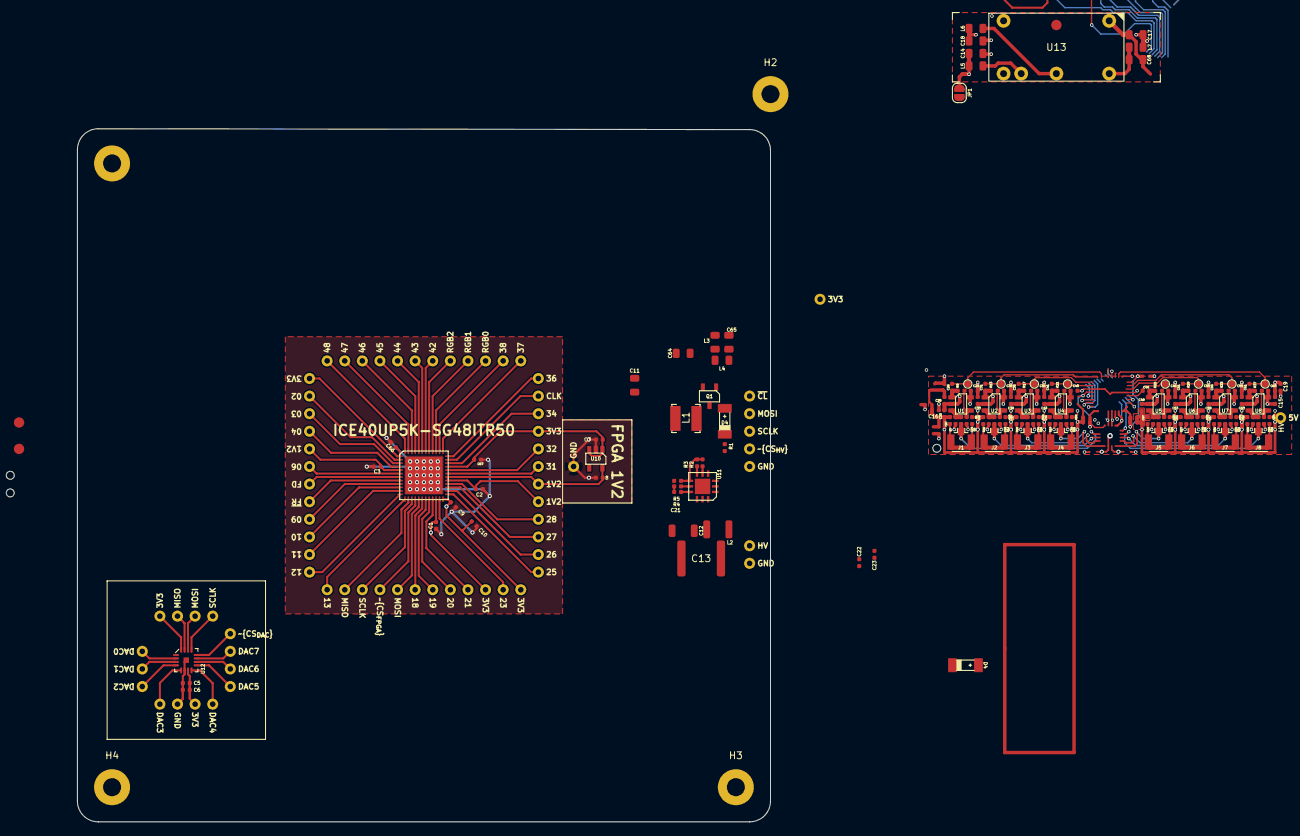
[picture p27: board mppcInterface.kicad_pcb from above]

Board: 2 copper layers, 100.0 x 100.0 mm, 228 parts (1 on the bottom side), 112 nets.

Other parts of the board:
D4#2: LL4148; SOD-80

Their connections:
unnamed 69: D4#2.2 (A); also elsewhere on the board
unnamed 70: D4#2.1 (K); also elsewhere on the board

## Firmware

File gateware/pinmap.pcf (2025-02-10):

# example.pcf

# Channels as inputs

set_io --warn-no-port CH0 31
set_io --warn-no-port CH1 32
set_io --warn-no-port CH2 1
set_io --warn-no-port CH3 2
set_io --warn-no-port CH4 20
set_io --warn-no-port CH5 22
set_io --warn-no-port CH6 23
set_io --warn-no-port CH7 26

set_io --warn-no-port LED0 30
set_io --warn-no-port LED1 29
set_io --warn-no-port LED2 27

# Output to Pi

set_io --warn-no-port gpioSDO 13 # Pin 13 is SDI on FPGA -> Pin 19, GPIO10, WiringPi 12, MOSI on RaspberryPi
set_io --warn-no-port gpioSDI 12 # Pin 12 is SDO on FPGA -> Pin 21, GPIO09, WiringPi 13, MISO on RaspberryPi
set_io --warn-no-port gpioSCK 15 # Pin 15 is SCK on FPGA -> Pin 23, GPIO11, WiringPi 14, SCK  on RaspberryPi
set_io --warn-no-port gpioSS  14 # Pin 14 is SS  on FPGA -> Pin 18, GPIO24, WiringPi 05, SS   on RaspberryPi

set_io --warn-no-port CLK     6  # Pin 6  on FPGA -> Pin 07, GPIO4, WiringPi 07, CLK on RaspberryPi

set_io --warn-no-port gpio18  7  # Pin 07 on FPGA -> Pin 12, GPIO18, WiringPi 01 on RaspberryPi 
set_io --warn-no-port gpio17  5  # Pin 05 on FPGA -> Pin 11, GPIO17, WiringPi 00 on RaspberryPi
set_io --warn-no-port gpio23  19 # Pin 19 on FPGA -> Pin 16, GPIO23, WiringPi 04 on RaspberryPi
set_io --warn-no-port gpio27  8  # Pin 08 on FPGA -> Pin 13, GPIO27, WiringPi 02 on RaspberryPi

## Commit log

2016-04-06 Cad model Built
    [1x1Angle.iam, 1x1Female.iam, 1x5Angle.iam, 1x6Female.iam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]
2016-04-22 Code has website and nodejs gpio control
    [mppcInterfacePcb.step]
2016-06-28 Changed to channel modules, still need a uC on board
2016-06-30 New step files, board outline added
    [mppcInterfacePcb.step]
2016-07-05 updated assembly
    [1x1Angle.iam, 1x1Female.iam, 1x5Angle.iam, 1x6Female.iam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]
2016-07-05 added 403C part
    [403C.ipt]
2016-07-06 Arduino Traces Started
2016-07-06 Power and GND to board out
2016-07-07 Copper Pours and step/decal files
    [mppcInterfacePcb.step]
2016-07-07 Fixed Switch
    [mppcInterfacePcb.step]
2016-07-08 Updated BOM
    [bom.xlsx]
2016-07-12 updated assemblies
    [MO-237 10005639-11109LF.ipt, MO-237.iam, body.ipt, mppcInterfacePcb.ipt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]
2016-07-12 updated board
2016-07-18 changed board
    [mppcInterface.iam, mppcInterfacePcb.ipt]
2016-07-22 Finished routing board
2016-07-25 Finished Board
    [mppcInterfacePcb.step]
2016-07-25 fixed board hole
    [mppcInterfacePcb.step]
2016-07-25 board thickness
    [mppcInterfacePcb.step]
2016-07-25 created 4 channel assembly
    [TSSOP.ipt, assembly.iam, body.ipt, body_MIR.ipt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]
2016-07-25 Fixed BOM
    [bom.xlsx]
2016-07-25 added pictures
    [11mm M2.5 standoff.ipt, M2.5 6mm screw.ipt, M2.5 hex nut.ipt, assembly.iam]
2016-08-03 updated parts
    [NPTC102KFMS-RC.iam, SHT3x-DIS.ipt, body.ipt, pin.ipt]
2016-08-09 added standoffs and updated assembly
    [11mm M2.5 standoff.ipt, M2.5 6mm screw.ipt, M2.5 hex nut.ipt, M2.5x10mm female female standoff.ipt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]
2016-08-26 Updated Board for new voltage inverter and I2C LLC
2016-10-13 Smaller board, more compact routing
2016-10-18 Boad completed ready for review
    [mppcInterfacePcb.step]
2016-10-19 Cad completed, needs logo, name, and accelerometer
    [11mm M2.5 standoff.ipt, 32 TQFP.ipt, 403C.ipt, 960240-6202-AR Body.ipt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]
2016-10-19 Replaced decals
    [mppcInterfacePcb.ipt]
2016-10-24 Added grounding pads, test pounts, fixed arduino master i2c swap
2017-01-07 Updated to 2017 inventor files, redid renders,updated submodule
    [capacitor-0402.ipt, capacitor.ipt, raspberry_pi_B+_(15_pin_FFC_Connector).SLDASM, raspberry_pi_B+_(168_FBGA_12x12).SLDPRT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]
2017-06-09 Changed surface mount pads to surface mount female headders, changed year to 2017
2019-01-06 New year, new branch, new design, new EDA tool. Readme to be updated soon
    [11mm M2.5 standoff.ipt, 32 TQFP.ipt, 403C.ipt, 960240-6202-AR Body.ipt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]
2019-01-06 renamef from HV
    [mppcInterface.kicad_pcb, mppcInterface.sch]
2019-01-12 Max1932 routed, fpga signal in router. Going to removed Voltage div here
    [MAX1932.sch, OPA846.sch, SRN4018.ipt, SRN4018.stp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]
2019-01-12 -5v supply, fpga routed
    [MAX1932.sch, mppcInterface.kicad_pcb, mppcInterface.sch]
2019-01-12 routing only PI side left
    [MAX1932.sch, mppcInterface.kicad_pcb]
2019-08-13 Wired up board
    [MAX1932.sch, OPA846.sch, mppcInterface.kicad_pcb, mppcInterface.sch]
2019-09-20 Changed inverter IC, added some decoupling
    [MAX1932.sch, OPA846.sch, mppcInterface.kicad_pcb, mppcInterface.sch]
2019-10-23 Finsihed layout for 1v2
    [MAX1932.sch, OPA846.sch, mppcInterface.kicad_pcb, mppcInterface.sch]
2019-10-23 Added more decopling, changed I2C jack to be compatible with 6P4C
    [OPA846.sch, mppcInterface.kicad_pcb, mppcInterface.sch]
2020-08-21 Initial update to 1.3
    [AMP-CH3OPA846.sch, BL-HUB37A-AV-TRB.stp, C-0201.stp, C-0402.stp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]
2021-01-27 updated readme a bit
    [OPA846.kicad_sch, bom.csv, mppcInterface.kicad_sch]
2025-02-09 Updating gateware
    [ICE40-UP5K-SG48I.STEP, OPA846.kicad_sch, S13360-2050VE 2.stp, U.FL 2.step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]

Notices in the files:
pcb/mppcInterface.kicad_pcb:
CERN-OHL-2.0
